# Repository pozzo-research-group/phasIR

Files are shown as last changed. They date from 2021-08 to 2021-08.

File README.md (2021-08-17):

 
 
 
 
 
 
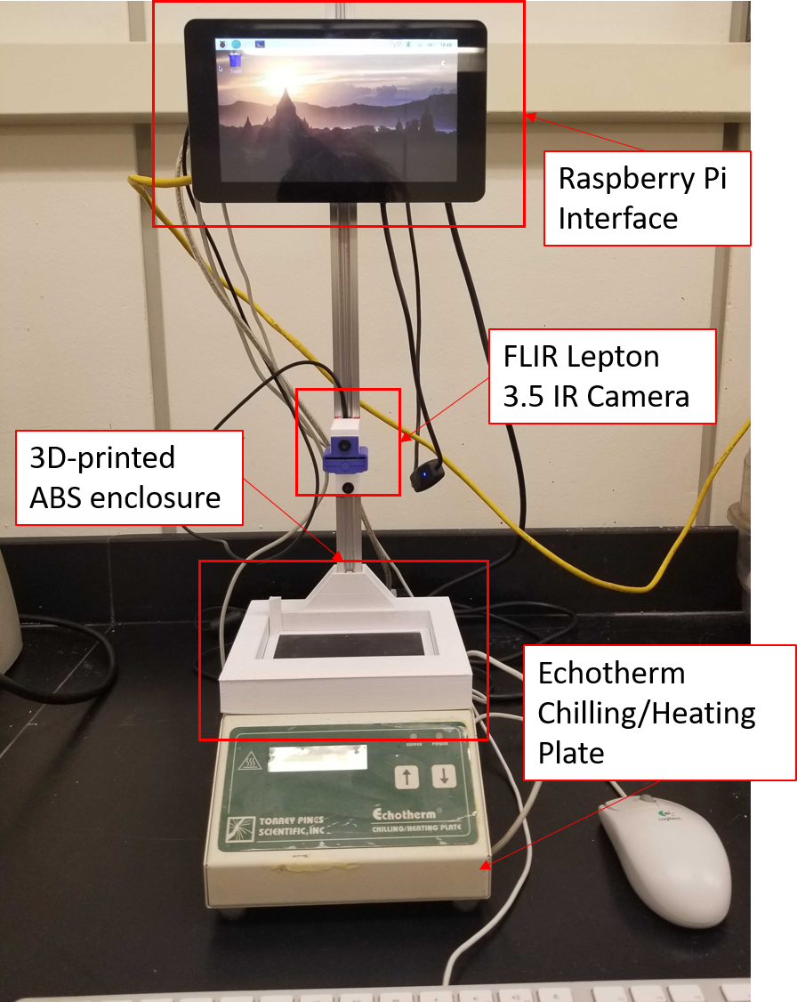
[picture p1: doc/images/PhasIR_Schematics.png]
Generat PhasIR Schematics. The system is composed by a Raspberry Pi Interface, a Lepton FLIR 3.5 IR Camera and a Echotherm IC25 Chilling/Heating plate


# phasIR

Python modules for high-throughput thermal analysis for fast and accurate estimation of phase transition temperatures for up to 96-samples analyzed simultaneously in under 15 minutes. The package includes the data analysis software, as well as build files to reproduce the PhasIR hardware infrastructure.

## The Hardware System

The hardware PhasIR system is composed of a **FLIR Lepton 3.5 IR camera** placed above a **Echotherm IC25 Chilling/Heating plate** and a **Raspberry Pi Interface**.

To ensure a constant sample position in the well across the entire temperature transition, the aluminum wellplate was designed with _conical-shaped wells_. The plate surface was also painted black to ensure an emissivity of one and improve the data collection.

The overall design of the PhasIR hardware system takes inspiration from Differential Thermal Analysis (DTA) techniques that operated on a single sample at a time. A black anodized aluminum plate is used as the reference point for the plate temperature, while the sample temperature is obtained at the center-point of the conical wells. All of this is collected simultaneously using the IR camera that captures the full view of the plate.

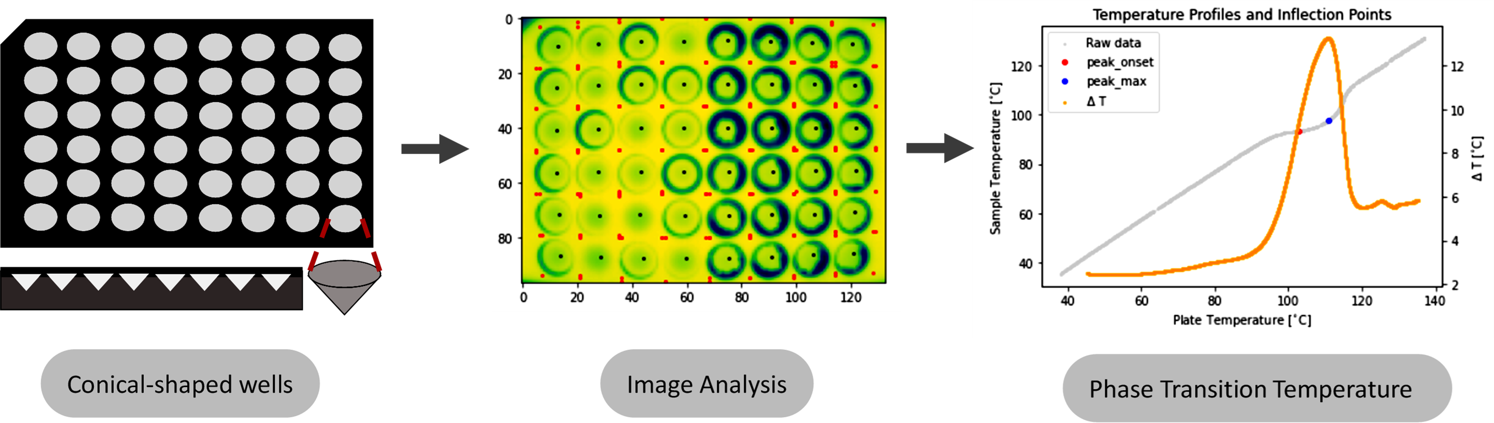
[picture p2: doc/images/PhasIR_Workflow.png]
General Workflow for PhasIR System


## Application

While others previously have also demonstrated the use of optical methods to extract thermal properties of pure substances, the same analysis can also be extended towards the investigation of mixtures. For example, we have utilized the PhasIR system described herein to also obtain melting points for deep eutectic solvents. Deep eutectic solvents (DES) are composed of two or more substances, typically a molecular hydrogen bond donor and a quaternary ammonium salt. When mixed at a specific molar ratio, there is a large depression in the freezing point of the mixture, compared to that of the individual pure substances. The design space for DES is incredibly large, and the utilization of high-throughput systems, such as PhasIR, will aid in the screening and discovery of low-melting point DESs that could find numerous uses as drug-delivery agents, clean energy electrolytes, green solvents, and many others.

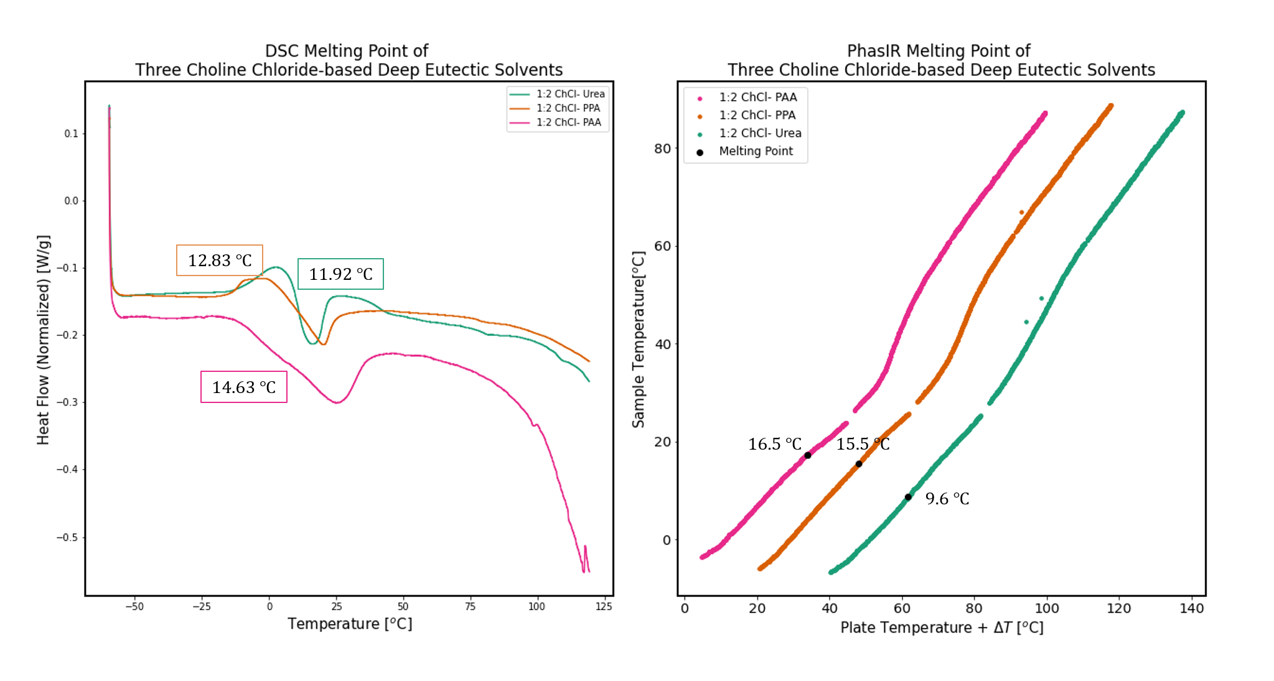
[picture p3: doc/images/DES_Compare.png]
Compare Melting point Temperature determination from Differential Scanning Calorimetry [left] and the PhasIR system [right]


## Requirements

_**Software**_:

The PhasIR package was written in Python and depends on various common libraries (pandas, numpy, scipy, matplotlib and scikit-image). Additionally, the proposed data analysis requires the use of Jupyter Notebook.

_**Hardware**_:

The hardware depended on the use of a Raspberry Pi and Lepton 3.5 IR camera with PureThermal 2 module.
The Raspberry Pi OS is required to initiate data collection on the all-in-one system. To capture thermal images using the FLIR Lepton 3.5 IR camera, the open-source image capture software <a href=https://github.com/Kheirlb/purethermal1-uvc-capture> purethermal1-uvc-capture</a> was used .

## Installation

The package PhasIR can be installed using following command:

<code>conda install -c pozzorg phasIR </code>

Alternatively, you can also install it using the GitHub repository as follows:

1. In your terminal, run <code>git clone https://github.com/pozzo-research-group/phasIR</code>
2. Change the directory to the phasIR root directory
3. Run <code>python setup.py install</code>
4. To check installation run, <code>python -c "import phasIR"</code> in your terminal

## Usage

### Image Analysis:

1. _Well position through automatic edge detection_ <a href=https://github.com/pozzo-research-group/phasIR/doc/examples/Example_Edge_Detection.ipynb> [Example notebook]</a>

* This method can be used for images(video frames) with high contrast and minimal noise which will allow for detection of edges of just the samples.
* The temperature profile of the samples and plate is automatically determined by detecting the edges, filling and labeling them, and monitoring the temperature at their centroids.
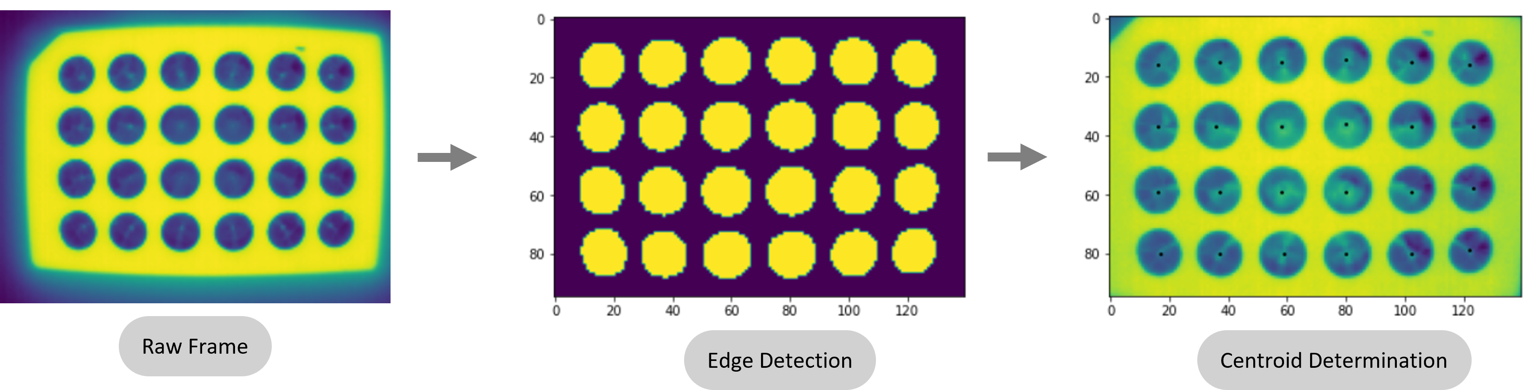
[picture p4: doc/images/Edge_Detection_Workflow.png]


2. _Well position through manual centroid selection_ <a href=https://github.com/pozzo-research-group/phasIR/doc/examples/Example_Manual_Well_Selection.ipynb> [Example notebook]</a>

* This is an alternative technique for low contrast images(video frames). In some situations, the automatic centroid detection cannot correctly determine all the wells. This can also be used if a different plate configuration is used.
* Alternatively, the centroid location for each sample can be manually selected on the pop-out figure

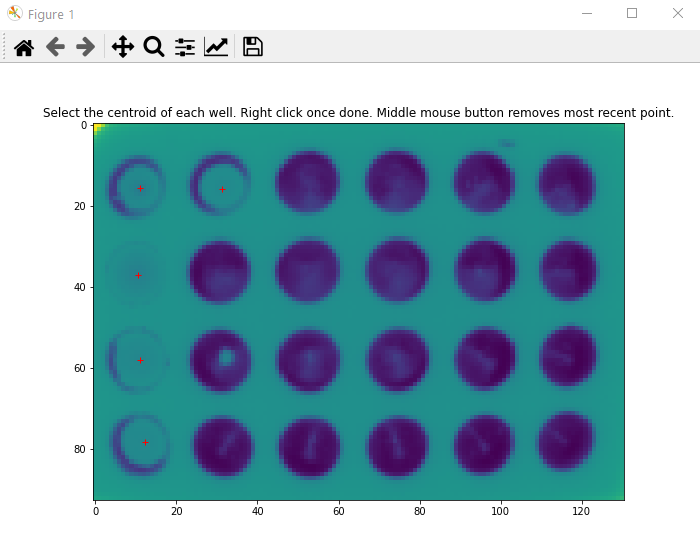
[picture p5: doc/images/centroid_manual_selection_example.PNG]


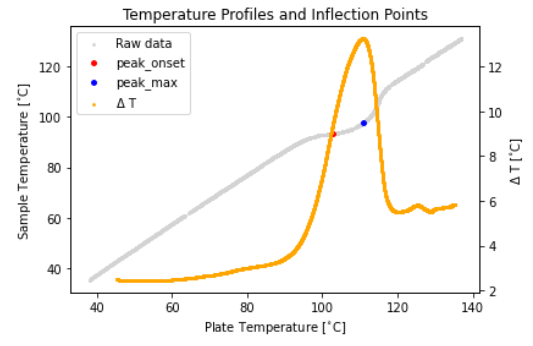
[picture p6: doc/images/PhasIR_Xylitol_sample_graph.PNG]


### Thermal Analysis

* An inflection is observed at the melting point in the temperature profile of the samples due to the following reasons

1. Change in thermal conductivity of the sample
2. Increase in thermal contact between the sample and the well plate

* The point of inflection in the temperature profile is determined by looking at the peak on the $\Delta$T curve, obtained as the sample temperature subtracted from the plate temperature. The onset position of the peak and the peak itself are reported.
* The temperature of the onset of the $\Delta$T curve is taken as the _phase transition temperature_

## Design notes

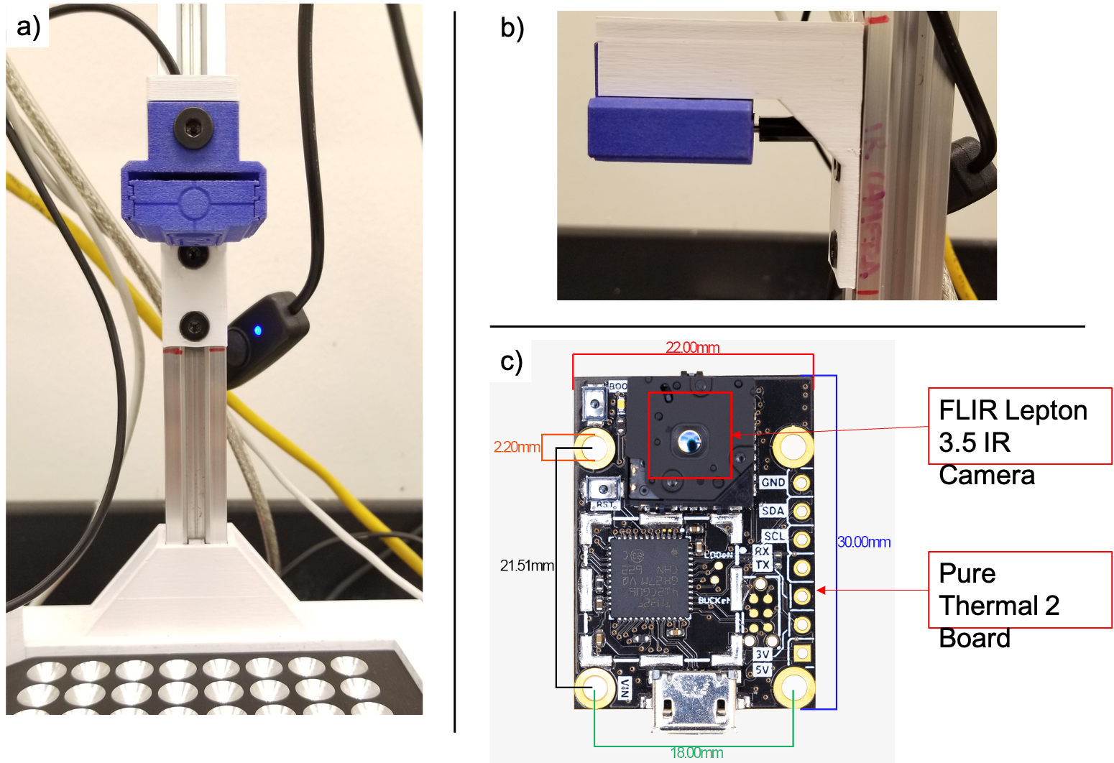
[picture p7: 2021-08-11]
doc/images/Camera_system_Schematics.png

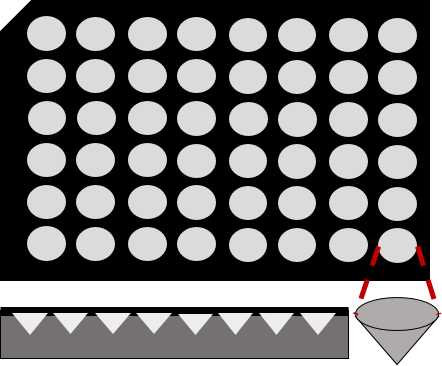
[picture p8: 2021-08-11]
doc/images/Conical-Well.png

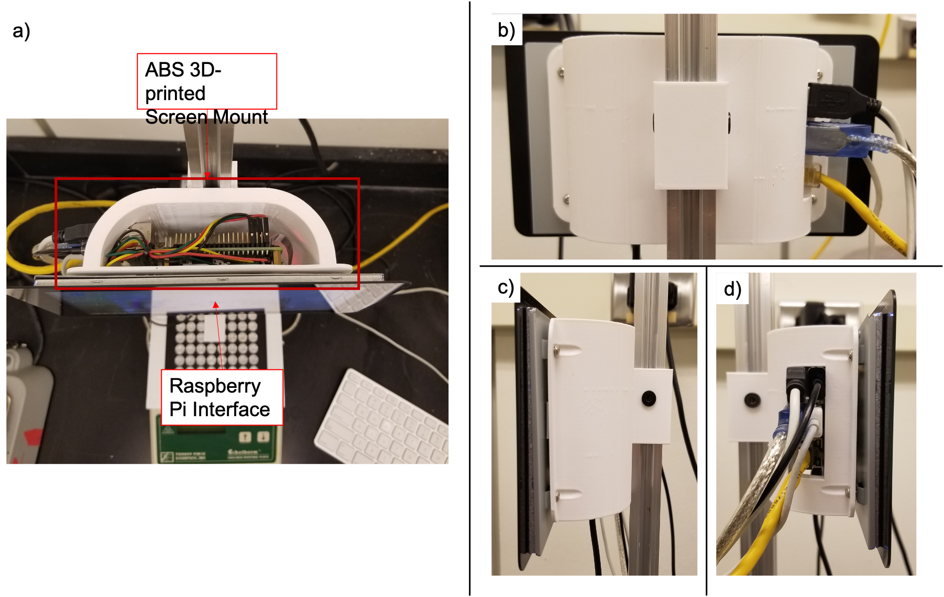
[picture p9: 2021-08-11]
doc/images/RaspPi_ABS_Mount.png

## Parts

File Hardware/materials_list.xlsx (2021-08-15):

Component | Catalog | Link | Price ($)
Lepton 3.5 Radiometric | 500-0771-01 | https://store.groupgets.com/products/flir-lepton-3-5?variant=6573007536155 | 199
PureThermal 2 - FLIR Lepton Smart I/O Module | PURETHERMAL-2 | https://store.groupgets.com/products/purethermal-2?variant=31873746665568 | 99
PureThermal 2 Case | PT2-CASE | https://store.groupgets.com/products/purethermal-2-case | 18.99
Raspberry Pi 3B+ | CanaKit Raspberry Pi 3 B+ (B Plus) with 2.5A Power Supply (UL Listed) | https://www.amazon.com/CanaKit-Raspberry-Power-Supply-Listed/dp/B07BC6WH7V | 59.99
Micro sdcard | SanDisk Ultra 32GB UHS-I/Class 10 Micro SDHC Memory Card With Adapter - SDSDQUAN-032G-G4A | https://www.amazon.com/SanDisk-Ultra-UHS-I-Memory-Adapter/ | 8.63
7inch Screen | Raspberry Pi Official 7 Inch Touch Screen for Raspberry Pi 4 / pi 3/pi 2 Model B | https://www.amazon.com/Raspberry-Pi-Official-Touch-Screen/dp/B073S3LQ6Q?s=electronics | 69.99
Echotherm IC25 Peltier Plate | LV41544737 | https://www.labx.com/item/torrey-pines-scientific-echotherm-ic25-digital-programmable/LV41544737 | 550
Anodized Aluminum Bar (Black, 6inx4inx0.5in) | 7083T46 | https://www.mcmaster.com/catalog/127/3982 | 32.01
ABS Filament | HATCHBOX ABS 3D Printer Filament, Dimensional Accuracy +/- 0.03 mm, 1 kg Spool, 1.75 mm, Beige | https://www.amazon.com/HATCHBOX-Printer-Filament-Dimensional-Accuracy/dp/B08PHYDBDG | 21.99
V-slot Rail | 150-LP | https://openbuildspartstore.com/v-slot-20x20-linear-rail/ | 5.49
USB to RS232 Cable (Male) | USB to Serial Adapter, Benfei USB to RS-232 Male (9-pin) | https://www.amazon.com/Serial-Adapter-Prolific-Chipset-Windows/dp/B0753HBT12?s=electronics | 8.59
Ethernet Cable (3ft) | Cat 7 Ethernet Cable, DanYee Nylon Braided 3ft CAT7 High Speed Professional Gold Plated | ZW5jcnlwdGVkUXVhbGlmaWVyPUFKMzA4Q0o1UURWMTAmZW5jcnlwdGVkSWQ9QTA3OTE3NjQyS1VLNjRXRFhHN1pDJmVuY3J5cHRlZEFkSWQ9QTAzNTE1MTkzNjRQWFBNNFZXRkY5JndpZGdldE5hbWU9c3BfYXRmJmFjdGlvbj1jbGlja1JlZGlyZWN0JmRvTm90TG9nQ2xpY2s9dHJ1ZQ | 5.94
 |  |  | Total ($)
 |  |  | 1079.62

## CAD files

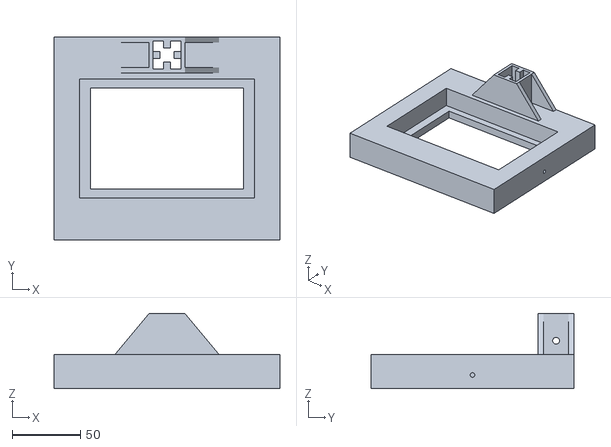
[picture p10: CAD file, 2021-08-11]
Hardware/Insulation Frame v7.stl
165.0 x 148.0 x 55.0

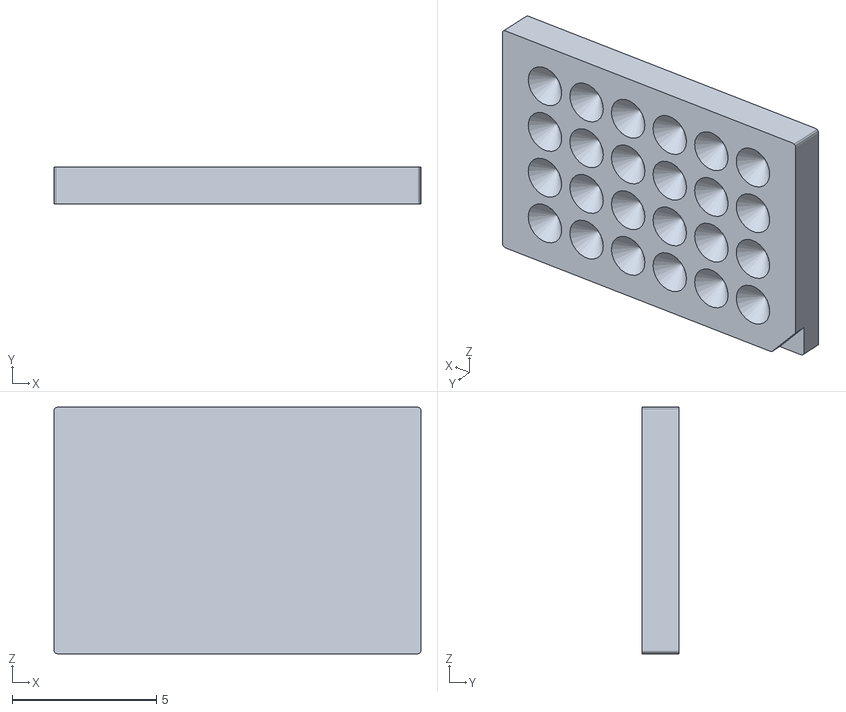
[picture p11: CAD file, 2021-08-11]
Hardware/24_wellplate_conical.stl
12.7 x 1.27 x 8.55

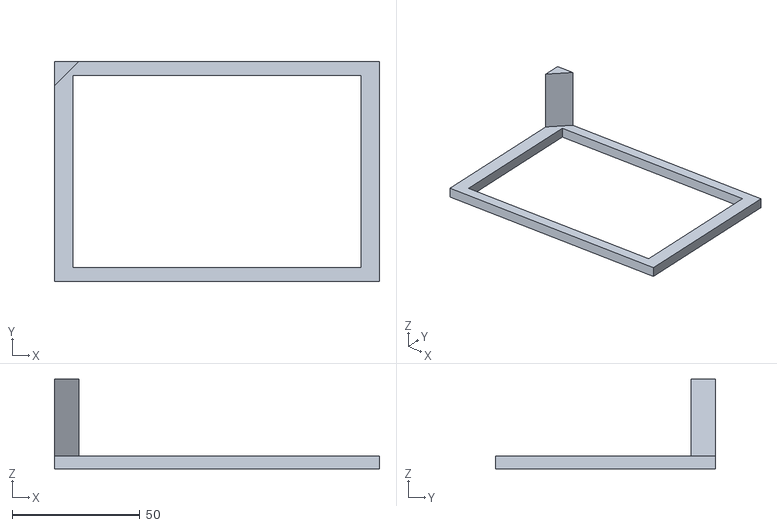
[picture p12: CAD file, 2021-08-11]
Hardware/Pull-Up Feature v4.stl
127.0 x 86.0 x 35.0

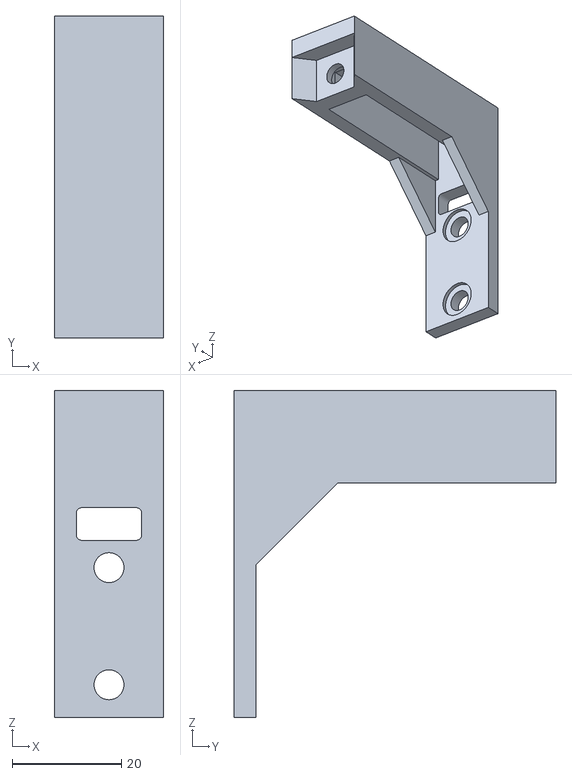
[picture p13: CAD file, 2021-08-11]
Hardware/Camera Frame v5.stl
20.0 x 59.0 x 60.0

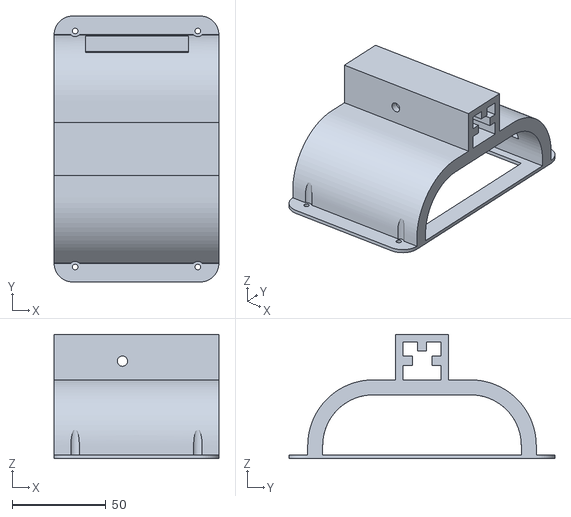
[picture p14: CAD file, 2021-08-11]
Hardware/Touchscreen Holder v2.stl
88.0 x 142.0 x 66.2

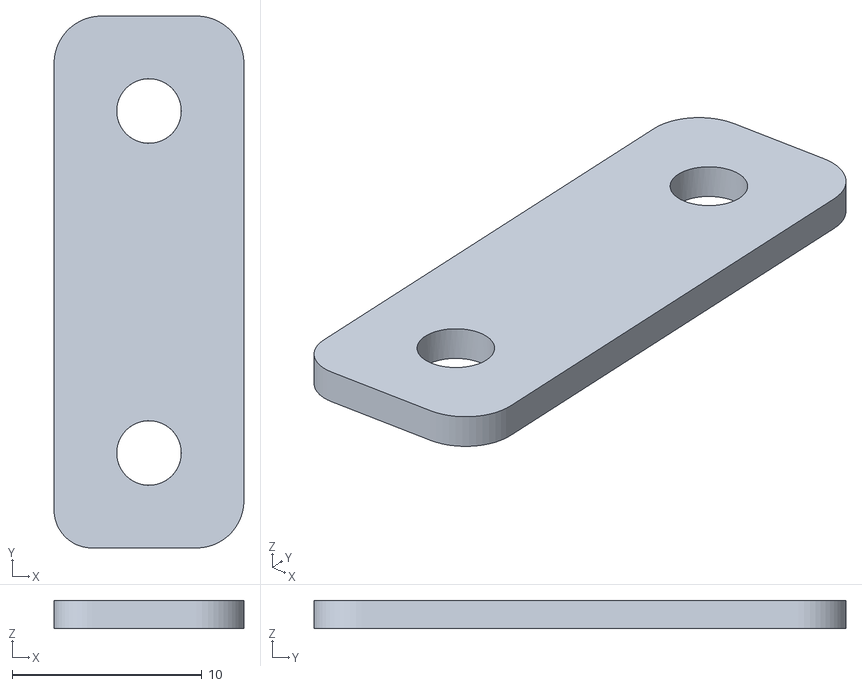
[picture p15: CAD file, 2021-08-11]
Hardware/Screw Clamp v1.stl
10.0 x 28.0 x 1.50

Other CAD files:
Hardware/96_wellplate_conical.stl
Hardware/48_wellplate_conical.stl

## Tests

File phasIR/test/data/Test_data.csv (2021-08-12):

 | Sample_temp 1 | Sample_temp 2 | Sample_temp 3 | Plate_temp 1 | Plate_temp 2 | Plate_temp 3
0 | -1.925507246376801 | -4.496956521739121 | -5.303188405797118 | 5.0675 | 0.64 | 0.0925
1 | -1.8820289855072405 | -4.449710144927521 | -5.235217391304359 | 5.18 | 0.76 | 0.3075
2 | -1.7542028985507203 | -4.30492753623188 | -5.13072463768116 | 5.2975 | 0.9075 | 0.4075
3 | -1.723768115942039 | -4.25347826086956 | -5.055942028985519 | 5.4075 | 1.09 | 0.45
4 | -1.7140579710144812 | -4.118405797101441 | -5.028405797101441 | 5.4525 | 1.11 | 0.5375
5 | -1.6494202898550794 | -4.058985507246361 | -4.995942028985519 | 5.5425 | 1.185 | 0.685
6 | -1.5443478260869596 | -3.9427536231884006 | -4.910869565217399 | 5.745 | 1.265 | 0.7375
7 | -1.4950724637681196 | -3.8481159420289988 | -4.809565217391318 | 5.91 | 1.54 | 0.985
8 | -1.4950724637681196 | -3.787391304347839 | -4.781884057971001 | 5.8975 | 1.5325 | 1.0
9 | -1.386231884057961 | -3.67217391304348 | -4.61289855072464 | 6.025 | 1.5775 | 1.14
10 | -1.393333333333321 | -3.6775362318840417 | -4.634492753623199 | 6.0375 | 1.6975 | 1.18
11 | -1.2684057971014409 | -3.5553623188405616 | -4.596811594202881 | 6.2175 | 1.9225 | 1.29
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

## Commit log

2021-08-12 Fixed test files and added data
    [Test_data.csv]
2021-08-14 Increased test coverage, fixed notebook import and spacing of print statement in data management module
2021-08-15 Adding list of materials
    [materials_list.xlsx]
